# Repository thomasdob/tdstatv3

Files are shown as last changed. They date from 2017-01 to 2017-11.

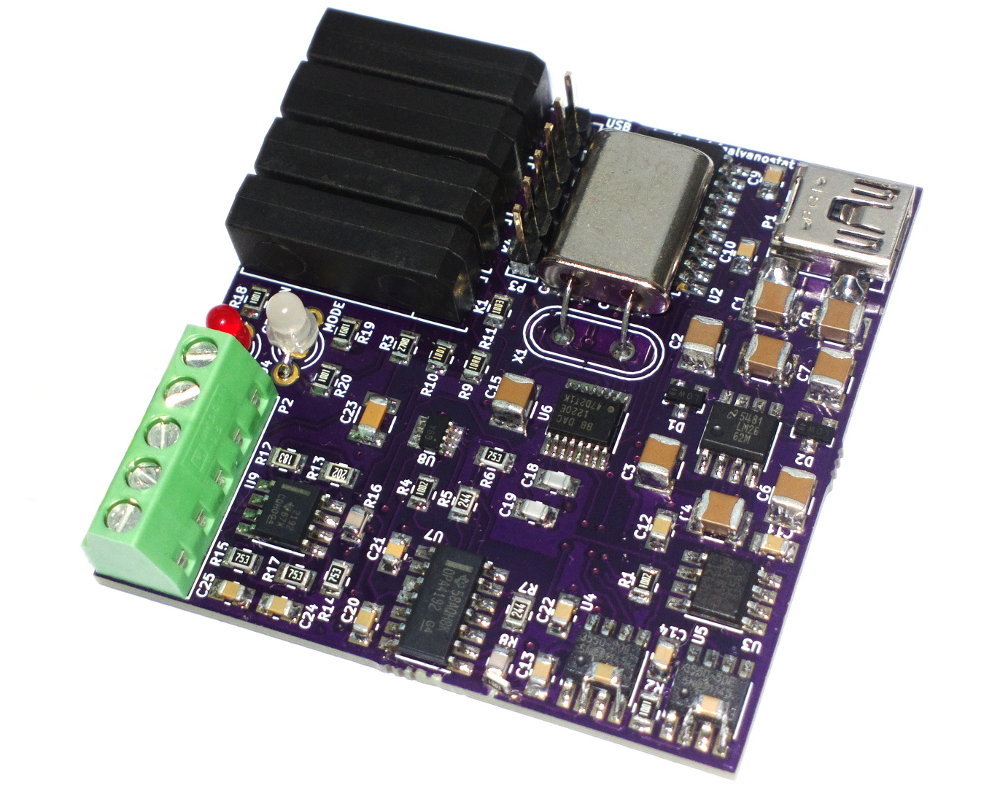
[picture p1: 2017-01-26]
photograph.jpg

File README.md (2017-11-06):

# TDstatv3
A USB-controlled potentiostat/galvanostat for thin-film battery characterization

## Introduction
This repository contains all the necessary design files to build your own USB-controlled potentiostat/galvanostat.
These files are intended as supplementary information accompanying the whitepaper at https://arxiv.org/pdf/1701.07650.pdf.

## Repository contents

### Directories
* `kicad`: KiCad design files (schematic diagram and PCB layout).
* `firmware`: Source code and compiled firmware for the PIC16F1459 microcontroller. Uses Microchip's XC8 compiler.
* `python`: Contains `tdstatv3.py`; run this file with Python 3 to bring up a GUI measurement tool.
* `gerber`: PCB design files in Gerber format, the universal standard for PCB manufacturing.
* `datasheets`: Datasheets in pdf format for the integrated circuits used in this design.
* `drivers`: Libusb drivers for Windows (not necessary on other operating systems).

### Files
* `full_schematic.pdf`: Complete schematic diagram in pdf format.
* `parts_list.txt`: Complete parts list, useful when ordering components.
* `pcb_3dview.png`: 3D renders of the PCB design, useful for verification of the PCB layout.
* `pcb_fabrication_diagram.pdf`: Front side of PCB with component locations and values, useful for circuit assembly.
* `photograph.jpg`: A photograph of the assembled circuit, using a PCB manufactured by [OSH Park](https://oshpark.com/).
* `LICENSE`: a copy of the GNU GPLv3 license.
* `README.md`: This file.

## USB access on Linux
In order to access the device without requiring root privileges, create a file
`/etc/udev/rules.d/99-tdstatv3.rules` containing the line

```
SUBSYSTEM=="usb", ATTRS{idVendor}=="a0a0", ATTRS{idProduct}=="0002", GROUP="plugdev", MODE="0666"
```
This assumes that the current user is a member of the `plugdev` group, and that the default USB Vendor and Product ID's
as coded in the microcontroller firmware are used; if not, these values need to be adjusted.

## Credits
* Thomas Dobbelaere
* email: thomas.dobbelaere@gmail.com

## License
The contents of this repository are licensed under the GNU General Public License (GPL).

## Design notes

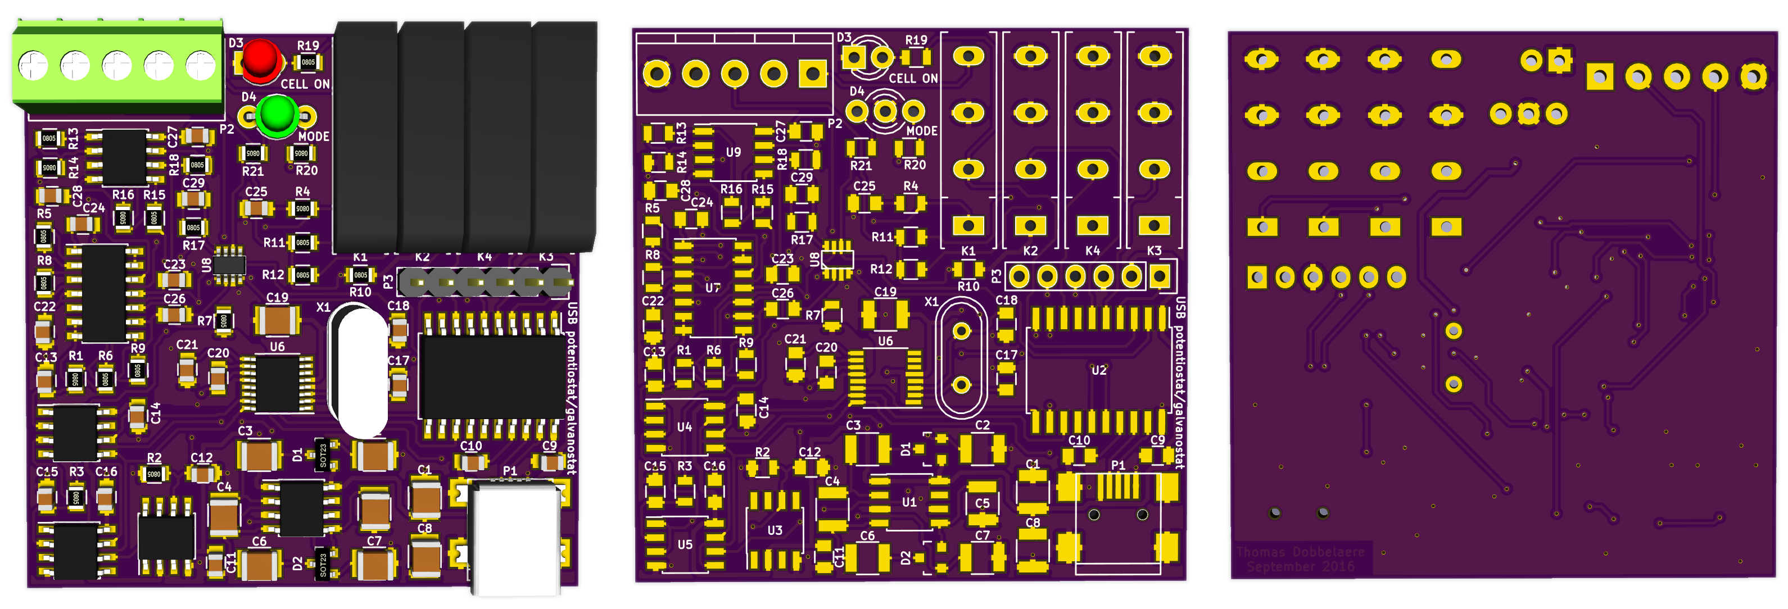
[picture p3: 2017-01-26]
pcb_3dview.png

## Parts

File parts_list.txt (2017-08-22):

Reference                     Description                                              Footprint     Digikey part #
R1,R3,R19-R21                 Resistor, 1k, 1%                                         0805          311-1.00KCRCT-ND
R2,R5                         Resistor, 10k, 1%                                        0805          311-10.0KCRCT-ND
R4                            Resistor, 27 ohm, 1%                                     0805          311-27.0CRCT-ND
R6,R8                         Precision resistor, 240k, 0.1% or better                 0805          RG20N240KWCT-ND
R7,R9,R15-R18                 Precision resistor, 75k, 0.1% or better                  0805          P75KBSCT-ND
R10                           Precision resistor, 10 ohm, 0.1% or better               0805          A119971CT-ND
R11                           Precision resistor, 1k, 0.1% or better                   0805          P1.0KDACT-ND
R12                           Precision resistor, 100k, 0.1% or better                 0805          P100KDACT-ND
R13                           Precision resistor, 18k, 0.1% or better                  0805          P18KDACT-ND
R14                           Precision resistor, 2k, 0.1% or better                   0805          P2.0KDACT-ND
C1-C8,C19                     Capacitor, 10 µF, ceramic                                1210          490-1867-1-ND
C9-C16, C22,C23,C25,C27,C28   Capacitor, 0.1 µF, ceramic                               0805          399-1168-1-ND
C17,C18,C26,C29               Capacitor, 12 pF, ceramic                                0805          1276-1120-1-ND
C20                           Capacitor, 3.3 nF, ceramic                               0805          399-10070-1-ND
C21                           Capacitor, 10 nF, ceramic                                0805          399-7992-1-ND
C24                           Capacitor, 4700 pF, ceramic                              0805          399-1155-1-ND
D1,D2                         Schottky diode, dual, BAT721S                            SOT-23        1727-3574-1-ND
D3                            LED, 3mm, red                                            -             754-1590-ND
D4                            LED, 3mm, dual red/green, common cathode                 -             754-1221-ND
U1                            Switched-capacitor voltage convertor, LM2662             SOIC-8        LM2662MX/NOPBCT-ND
U2                            8-bit USB microcontroller, PIC16F1459                    SOIC-20W      PIC16F1459-I/SO-ND
U3                            2.5V voltage reference, ADR421                           SOIC-8        ADR421ARZ-ND
U4,U5                         A/D convertor, MCP3550 (choose suffix by region)         SOIC-8        MCP3550-50(60)E/SN-ND
U6                            D/A convertor, DAC1220                                   SSOP-16       DAC1220E-ND
U7                            Op-amp, quad, OPA4192                                    SOIC-14       296-43159-1-ND
U8                            SPDT analog switch, DG449                                SOT-23-8      DG449DS-T1-E3CT-ND
U9                            Op-amp, dual, OPA2192                                    SOIC-8        296-42106-1-ND
X1                            Crystal oscillator, 2.5 MHz                              HC49          X1003-ND
K1-K4                         Reed relay, Coto 9007-05-01                              SIP           306-1063-ND
P1                            Mini USB receptacle, surface mount, type B               -             609-4700-1-ND
P2                            Terminal block, through hole, 5 position, 3.5mm spacing  -             277-5827-ND
P3                            Pin header, through hole, 6 pin                          -             S1011EC-06-ND

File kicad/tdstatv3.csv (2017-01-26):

Reference | Value | Footprint | Datasheet
U1 | LM2662 | Housings_SOIC:SOIC-8_3.9x4.9mm_Pitch1.27mm
C5 | 10 µF | Capacitors_SMD:C_1210
C6 | 10 µF | Capacitors_SMD:C_1210
C7 | 10 µF | Capacitors_SMD:C_1210
C4 | 10 µF | Capacitors_SMD:C_1210
D2 | BAT721S | TO_SOT_Packages_SMD:SOT-23
C3 | 10 µF | Capacitors_SMD:C_1210
D1 | BAT721S | TO_SOT_Packages_SMD:SOT-23
C2 | 10 µF | Capacitors_SMD:C_1210
U4 | MCP3550 | Housings_SOIC:SOIC-8_3.9x4.9mm_Pitch1.27mm
U6 | DAC1220 | Housings_SSOP:SSOP-16_3.9x4.9mm_Pitch0.635mm
U3 | ADR421 | Housings_SOIC:SOIC-8_3.9x4.9mm_Pitch1.27mm
U2 | PIC16F1459 | Housings_SOIC:SOIC-20W_7.5x12.8mm_Pitch1.27mm
P1 | Mini USB | Connect:USB_Mini-B
C11 | 0.1 µF | Capacitors_SMD:C_0805
C12 | 0.1 µF | Capacitors_SMD:C_0805
X1 | 2.5 MHz | Crystals:Crystal_HC49-U_Vertical
C17 | 12 pF | Capacitors_SMD:C_0805
C18 | 12 pF | Capacitors_SMD:C_0805
C21 | 10 nF | Capacitors_SMD:C_0805
C20 | 3.3 nF | Capacitors_SMD:C_0805
C19 | 10 µF | Capacitors_SMD:C_1210
U7 | OPA4192 | Housings_SOIC:SOIC-14_3.9x8.7mm_Pitch1.27mm
C25 | 0.1 µF | Capacitors_SMD:C_0805
R4 | 27R | Resistors_SMD:R_0805
C24 | 4700 pF | Capacitors_SMD:C_0805
R5 | 10k | Resistors_SMD:R_0805
K1 | 9007-05-01 | my_footprints:RELAY-9007
R6 | 240k* | Resistors_SMD:R_0805
R8 | 240k* | Resistors_SMD:R_0805
R7 | 75k* | Resistors_SMD:R_0805
R9 | 75k* | Resistors_SMD:R_0805
U5 | MCP3550 | Housings_SOIC:SOIC-8_3.9x4.9mm_Pitch1.27mm
C27 | 0.1 µF | Capacitors_SMD:C_0805
C28 | 0.1 µF | Capacitors_SMD:C_0805
C22 | 0.1 µF | Capacitors_SMD:C_0805
C23 | 0.1 µF | Capacitors_SMD:C_0805
C10 | 0.1 µF | Capacitors_SMD:C_0805
C9 | 0.1 µF | Capacitors_SMD:C_0805
P3 | ICSP | Pin_Headers:Pin_Header_Straight_1x06
D3 | CELL ON LED | LEDs:LED-3MM
D4 | MODE LED | my_footprints:DUO-LED-3mm
R19 | 1k | Resistors_SMD:R_0805
R20 | 1k | Resistors_SMD:R_0805
R21 | 1k | Resistors_SMD:R_0805
R10 | 10R* | Resistors_SMD:R_0805
R11 | 1k* | Resistors_SMD:R_0805
R12 | 100k* | Resistors_SMD:R_0805
U8 | DG449 | my_footprints:sot23-8
C14 | 0.1 µF | Capacitors_SMD:C_0805
C16 | 0.1 µF | Capacitors_SMD:C_0805
R2 | 10k | Resistors_SMD:R_0805
R3 | 1k | Resistors_SMD:R_0805
K2 | 9007-05-01 | my_footprints:RELAY-9007
K3 | 9007-05-01 | my_footprints:RELAY-9007
K4 | 9007-05-01 | my_footprints:RELAY-9007
R14 | 2k* | Resistors_SMD:R_0805
R13 | 18k* | Resistors_SMD:R_0805
R16 | 75k* | Resistors_SMD:R_0805
R15 | 75k* | Resistors_SMD:R_0805
R18 | 75k* | Resistors_SMD:R_0805
R17 | 75k* | Resistors_SMD:R_0805
U9 | OPA2192 | Housings_SOIC:SOIC-8_3.9x4.9mm_Pitch1.27mm
P2 | CELL | my_footprints:TerminalBlock_Phoenix_MKDS1_5_3mm5
C1 | 10 µF | Capacitors_SMD:C_1210
C8 | 10 µF | Capacitors_SMD:C_1210
R1 | 1k | Resistors_SMD:R_0805
C15 | 0.1 µF | Capacitors_SMD:C_0805
C13 | 0.1 µF | Capacitors_SMD:C_0805
C29 | 12 pF | Capacitors_SMD:C_0805
C26 | 12 pF | Capacitors_SMD:C_0805

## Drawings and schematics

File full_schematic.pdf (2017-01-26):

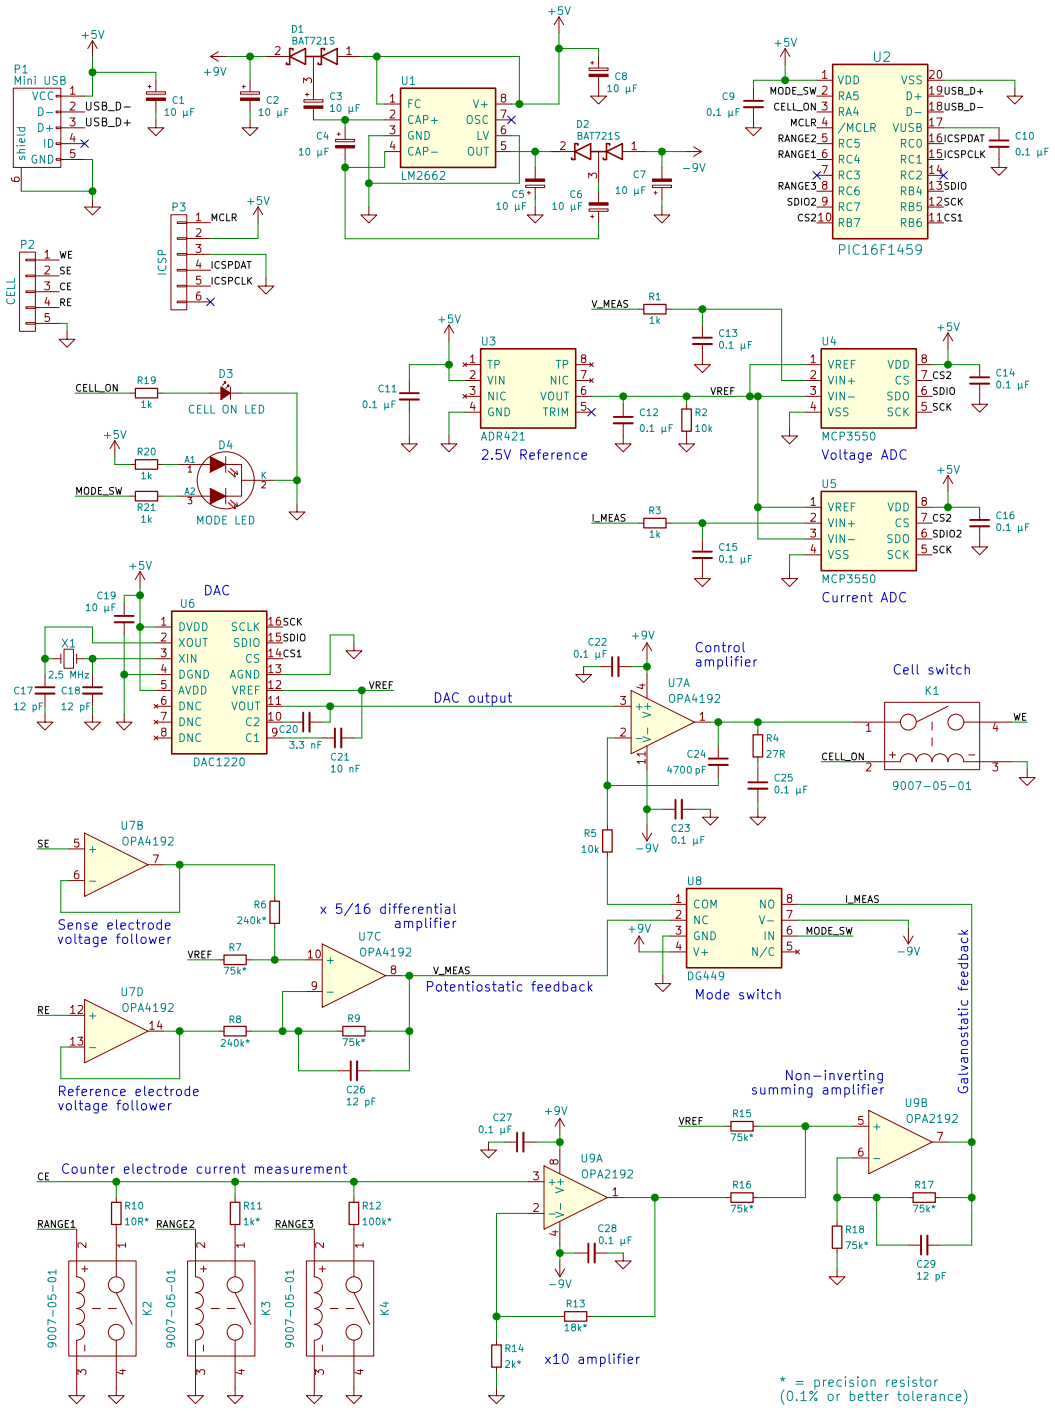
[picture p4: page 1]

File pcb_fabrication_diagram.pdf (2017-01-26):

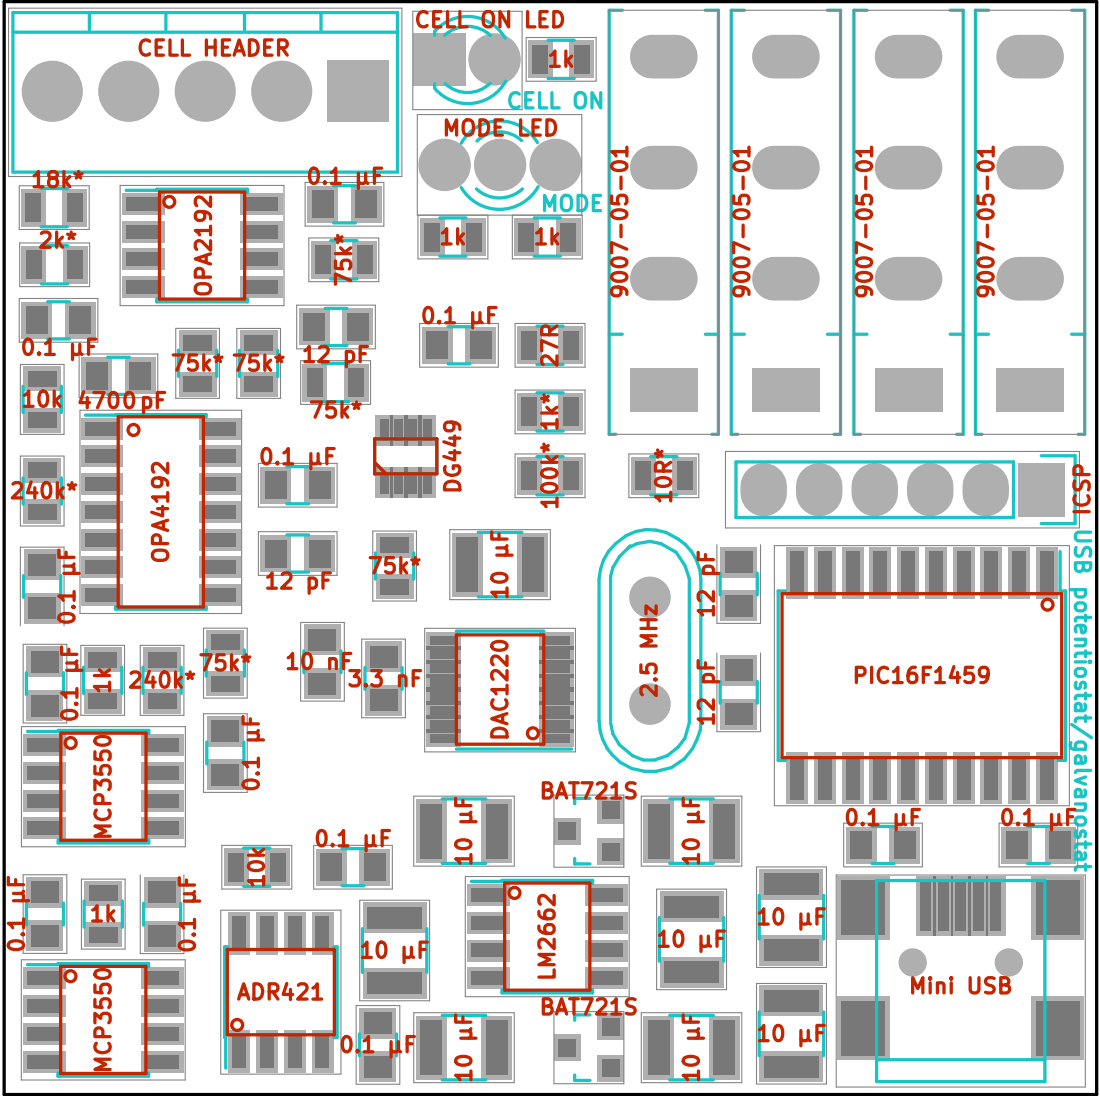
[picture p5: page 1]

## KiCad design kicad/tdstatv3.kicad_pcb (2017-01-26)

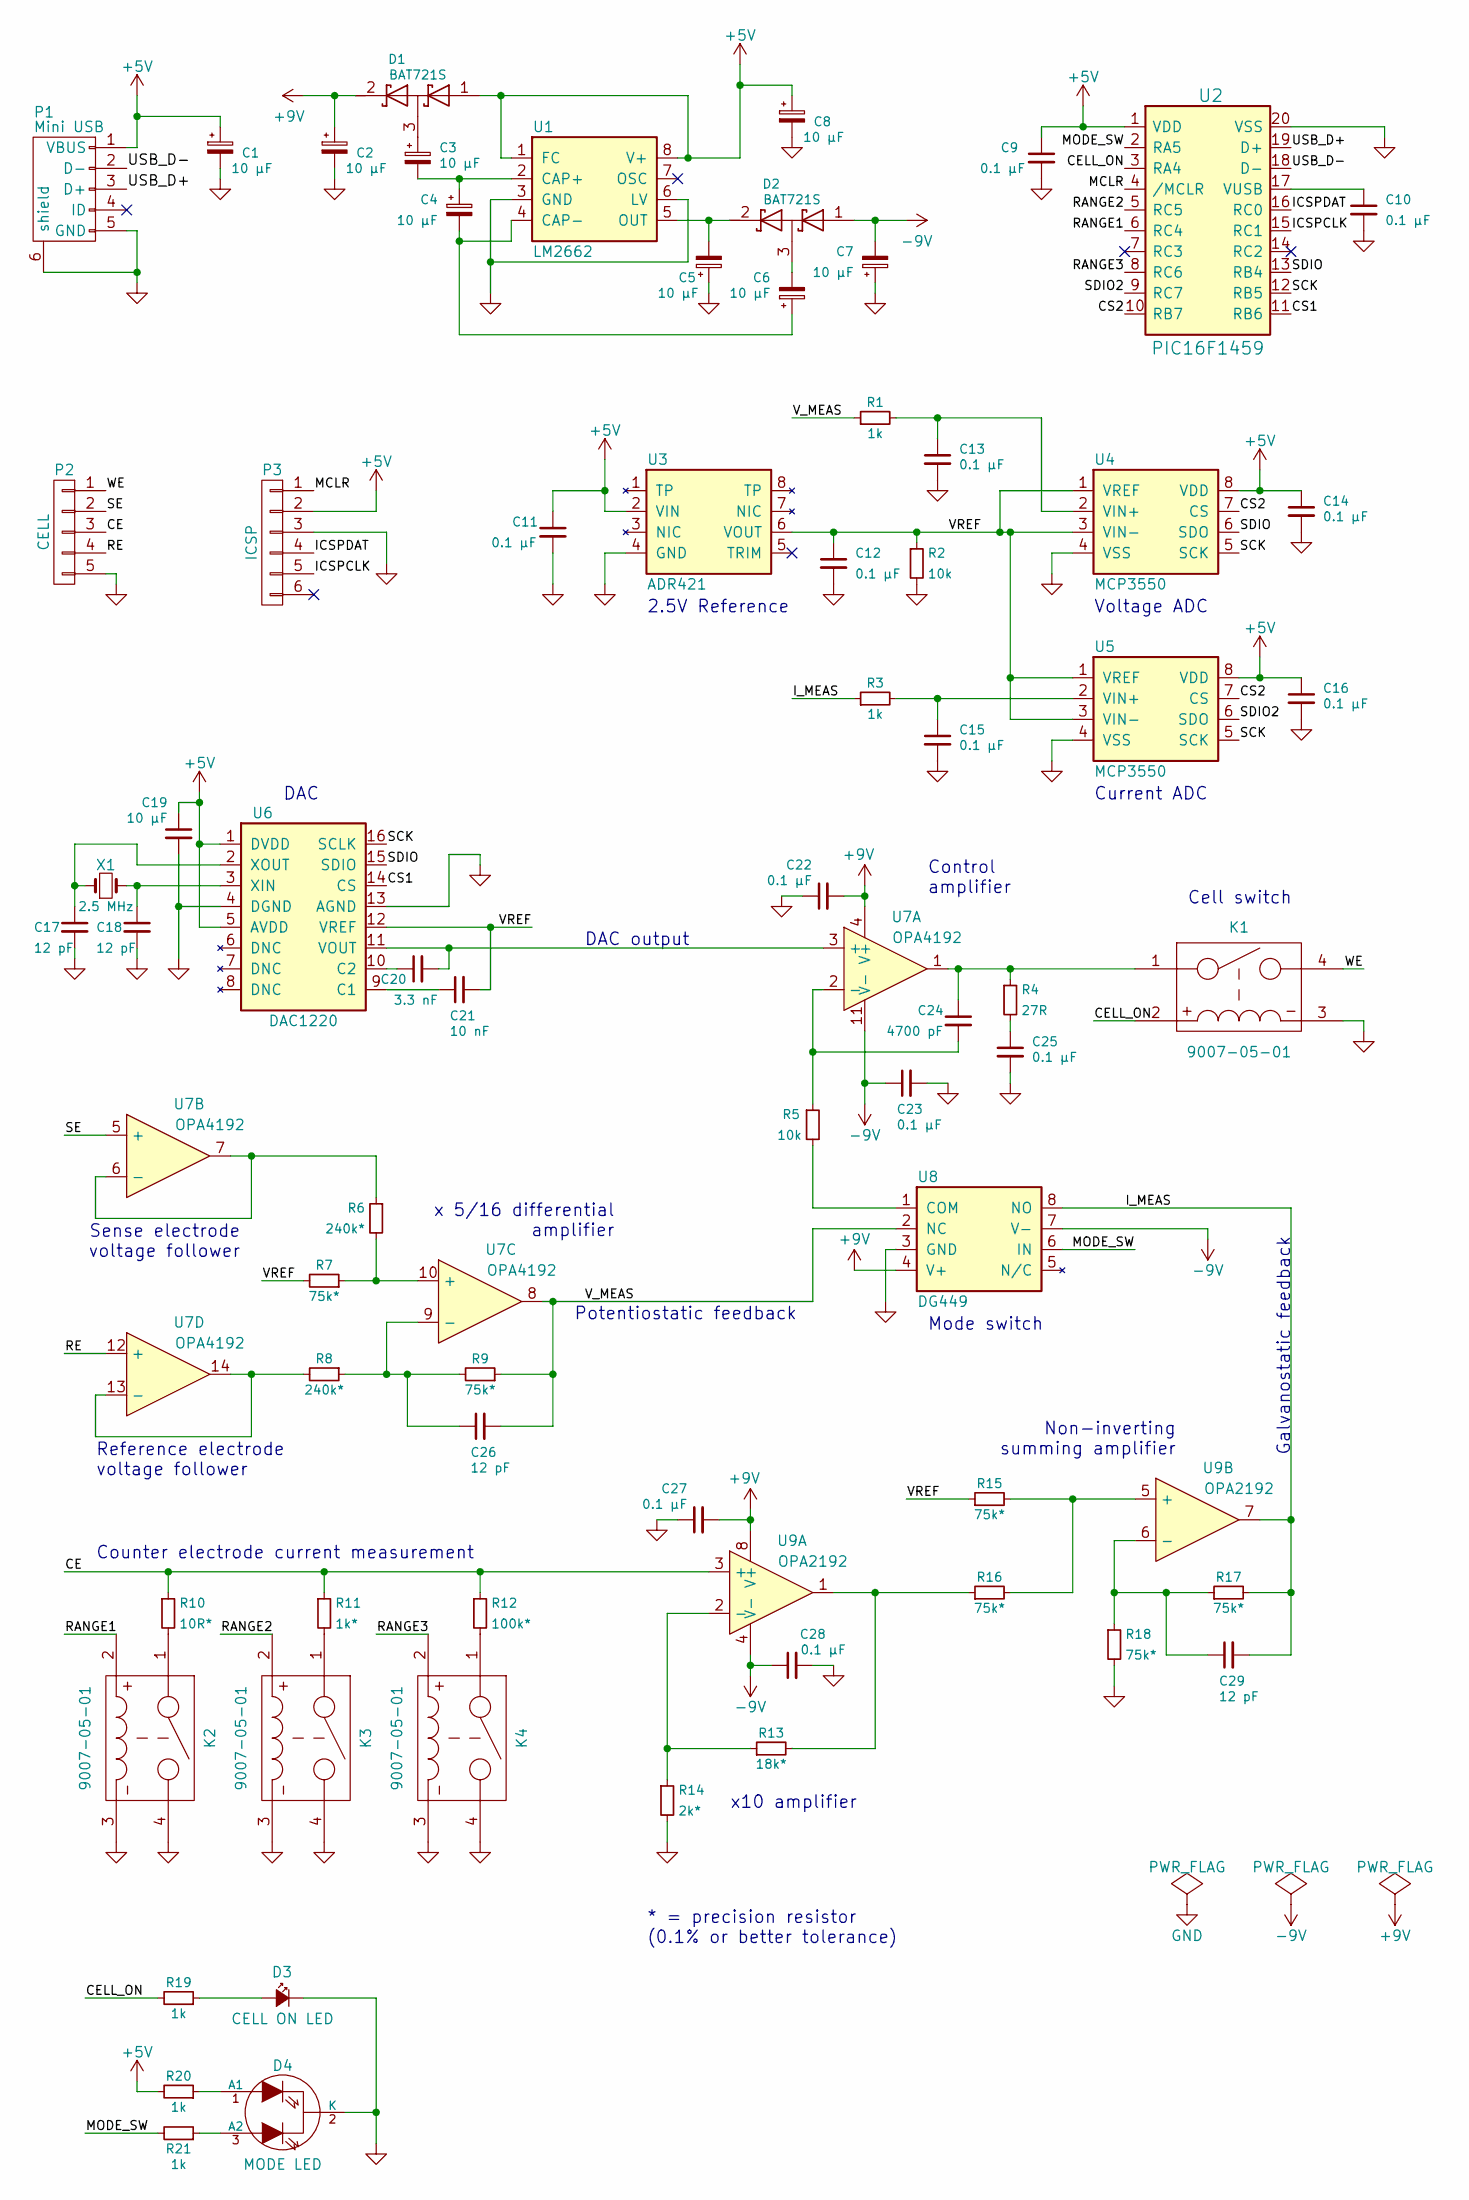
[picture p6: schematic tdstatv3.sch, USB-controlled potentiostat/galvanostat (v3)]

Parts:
C1, C2, C3, C4, C5, C6, C7, C8, C19: 10 µF; C_1210
C9, C10, C11, C12, C13, C14, C15, C16, C22, C23, C25, C27, C28: 0.1 µF; C_0805
C17, C18, C26, C29: 12 pF; C_0805
C20: 3.3 nF; C_0805
C21: 10 nF; C_0805
C24: 4700 pF; C_0805
D1, D2: BAT721S; SOT-23
D3: CELL ON LED; LED-3MM
D4: MODE LED; DUO-LED-3mm
K1, K2, K3, K4: 9007-05-01; RELAY-9007
P1: Mini USB; USB_Mini-B
P2: CELL; TerminalBlock_Phoenix_MKDS1_5_3mm5
P3: ICSP; Pin_Header_Straight_1x06
R1, R3, R19, R20, R21: 1k; R_0805
R2, R5: 10k; R_0805
R4: 27R; R_0805
R6, R8: 240k*; R_0805
R7, R9, R15, R16, R17, R18: 75k*; R_0805
R10: 10R*; R_0805
R11: 1k*; R_0805
R12: 100k*; R_0805
R13: 18k*; R_0805
R14: 2k*; R_0805
U1: LM2662; SOIC-8_3.9x4.9mm_Pitch1.27mm
U2: PIC16F1459; SOIC-20W_7.5x12.8mm_Pitch1.27mm
U3: ADR421; SOIC-8_3.9x4.9mm_Pitch1.27mm
U4, U5: MCP3550; SOIC-8_3.9x4.9mm_Pitch1.27mm
U6: DAC1220; SSOP-16_3.9x4.9mm_Pitch0.635mm
U7: OPA4192; SOIC-14_3.9x8.7mm_Pitch1.27mm
U8: DG449; sot23-8
U9: OPA2192; SOIC-8_3.9x4.9mm_Pitch1.27mm
X1: 2.5 MHz; Crystal_HC49-U_Vertical

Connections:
+5V: C1.1, C8.1, C9.1, C11.1, C14.1, C16.1, C19.1, D1.1 (A), P1.1 (VBUS), P3.2, R20.2, U1.1 (FC), U1.8 (V+), U2.1 (VDD), U3.2 (VIN), U4.8 (VDD), U5.8 (VDD), U6.1 (DVDD), U6.5 (AVDD)
+9V: C2.1, C22.2, C27.2, D1.2 (K), U7.4 (V+), U8.4 (V+), U9.8 (V+)
-9V: C7.2, C23.1, C28.1, D2.1 (A), U7.11 (V-), U8.7 (V-), U9.4 (V-)
/CE: P2.3, R10.1, R11.1, R12.1, U9.3 (+)
/CELL_ON: K1.2 (+), R19.2, U2.3 (RA4)
/CS1: U2.11 (RB6), U6.14 (CS)
/CS2: U2.10 (RB7), U4.7 (CS), U5.7 (CS)
/ICSPCLK: P3.5, U2.15 (RC1)
/ICSPDAT: P3.4, U2.16 (RC0)
/I_MEAS: C29.2, R3.1, R17.2, U8.8 (NO), U9.7
/MCLR: P3.1, U2.4 (/MCLR)
/MODE_SW: R21.2, U2.2 (RA5), U8.6 (IN)
/RANGE1: K2.2 (+), U2.6 (RC4)
/RANGE2: K3.2 (+), U2.5 (RC5)
/RANGE3: K4.2 (+), U2.8 (RC6)
/RE: P2.4, U7.12 (+)
/SCK: U2.12 (RB5), U4.5 (SCK), U5.5 (SCK), U6.16 (SCLK)
/SDIO: U2.13 (RB4), U4.6 (SDO), U6.15 (SDIO)
/SDIO2: U2.9 (RC7), U5.6 (SDO)
/SE: P2.2, U7.5 (+)
/USB_D+: P1.3 (D+), U2.19 (D+)
/USB_D-: P1.2 (D-), U2.18 (D-)
/VREF: C12.1, C21.2, R2.1, R7.2, R15.1, U3.6 (VOUT), U4.1 (VREF), U4.3 (VIN-), U5.1 (VREF), U5.3 (VIN-), U6.12 (VREF)
/V_MEAS: C26.2, R1.1, R9.1, U7.8, U8.2 (NC)
/WE: K1.4, P2.1
GND: C1.2, C2.2, C5.1, C7.1, C8.2, C9.2, C10.2, C11.2, C12.2, C13.2, C14.2, C15.2, C16.2, C17.2, C18.2, C19.2, C22.1, C23.2, C25.2, C27.1, C28.2, D3.1 (K), D4.2 (K), K1.3, K2.3, K2.4, K3.3, K3.4, K4.3, K4.4, P1.5 (GND), P1.6 (shield), P2.5, P3.3, R2.2, R14.2, R18.2, U1.3 (GND), U1.6 (LV), U2.20 (VSS), U3.4 (GND), U4.4 (VSS), U5.4 (VSS), U6.4 (DGND), U6.13 (AGND), U8.3 (GND)
unnamed: C3.1, D1.3 (common)
unnamed: C3.2, C4.1, U1.2 (CAP+)
unnamed: C4.2, C6.1, U1.4 (CAP-)
unnamed: C5.2, D2.2 (K), U1.5 (OUT)
unnamed: C6.2, D2.3 (common)
unnamed: C10.1, U2.17 (VUSB)
unnamed: C13.1, R1.2, U4.2 (VIN+)
unnamed: C15.1, R3.2, U5.2 (VIN+)
unnamed: C17.1, U6.2 (XOUT), X1.1
unnamed: C18.1, U6.3 (XIN), X1.2
unnamed: C20.1, U6.10 (C2)
unnamed: C20.2, U6.11 (VOUT), U7.3 (+)
unnamed: C21.1, U6.9 (C1)
unnamed: C24.1, K1.1, R4.1, U7.1
unnamed: C24.2, R5.1, U7.2 (-)
unnamed: C25.1, R4.2
unnamed: C26.1, R8.1, R9.2, U7.9 (-)
unnamed: C29.1, R17.1, R18.1, U9.6 (-)
unnamed: D3.2 (A), R19.1
unnamed: D4.1 (A1), R20.1
unnamed: D4.3 (A2), R21.1
unnamed: K2.1, R10.2
unnamed: K3.1, R11.2
unnamed: K4.1, R12.2
unnamed: R5.2, U8.1 (COM)
unnamed: R6.1, U7.6 (-), U7.7
unnamed: R6.2, R7.1, U7.10 (+)
unnamed: R8.2, U7.13 (-), U7.14
unnamed: R13.1, R14.1, U9.2 (-)
unnamed: R13.2, R16.1, U9.1
unnamed: R15.2, R16.2, U9.5 (+)

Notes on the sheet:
x 5/16 differential amplifier
Sense electrode voltage follower
Reference electrode voltage follower
Counter electrode current measurement
x10 amplifier
Non-inverting summing amplifier
Potentiostatic feedback
Galvanostatic feedback
Current ADC
Voltage ADC
2.5V Reference
Control amplifier
DAC
Mode switch
Cell switch
DAC output
* = precision resistor (0.1% or better tolerance)

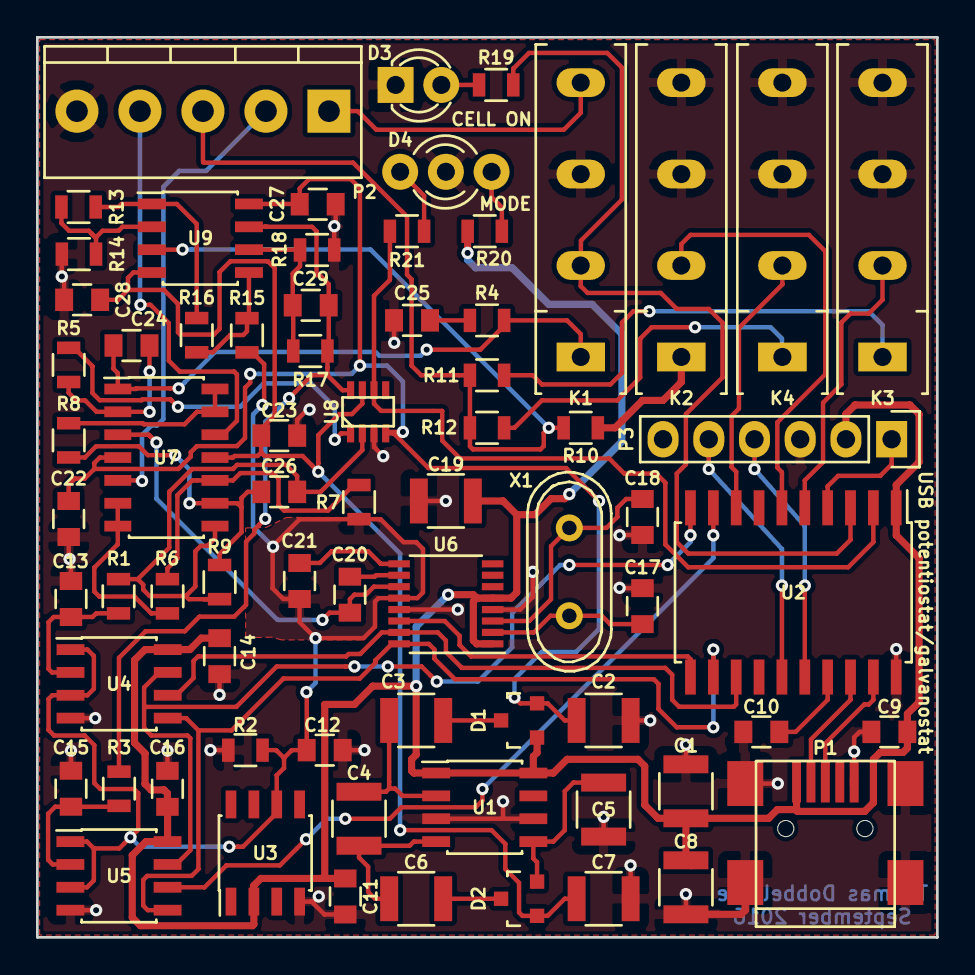
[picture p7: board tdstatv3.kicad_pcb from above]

Board: 2 copper layers, 50.0 x 50.0 mm, 71 parts (0 on the bottom side), 57 nets.

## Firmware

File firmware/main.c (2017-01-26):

/*
 * USB Potentiostat/galvanostat firmware
 *
 * This code makes use of Signal 11's M-Stack USB stack to implement 
 * communication through raw USB bulk transfers. Commands are received
 * as ASCII strings on EP1 OUT. They are then interpreted and executed;
 * they either change the state of output pins, or cause data to be read
 * from / written to the MCP3550 (ADC) or DAC1220 (DAC) using a software
 * SPI implementation. The resulting data, or an "OK" message, is sent as
 * a reply on EP1 IN. The USB service is interrupt-driven.
 *
 * Thomas Dobbelaere
 * CoCooN research group
 * 2016-06-07
 */

#include "usb.h"
#include <xc.h>
#include <string.h>
#include "usb_config.h"
#include "usb_ch9.h"
#include "spi_software.h"
#include "Flash.h"
#include "HEFlash.h"

// PIC16F1459 configuration bit settings:
// CONFIG1
#pragma config FOSC = INTOSC    // Oscillator Selection Bits (INTOSC oscillator: I/O function on CLKIN pin)
#pragma config WDTE = OFF       // Watchdog Timer Enable (WDT disabled)
#pragma config PWRTE = OFF      // Power-up Timer Enable (PWRT disabled)
#pragma config MCLRE = OFF      // MCLR Pin Function Select (MCLR/VPP pin function is digital input)
#pragma config CP = OFF         // Flash Program Memory Code Protection (Program memory code protection is disabled)
#pragma config BOREN = ON       // Brown-out Reset Enable (Brown-out Reset enabled)
#pragma config CLKOUTEN = OFF   // Clock Out Enable (CLKOUT function is disabled. I/O or oscillator function on the CLKOUT pin)
#pragma config IESO = OFF       // Internal/External Switchover Mode (Internal/External Switchover Mode is disabled)
#pragma config FCMEN = OFF      // Fail-Safe Clock Monitor Enable (Fail-Safe Clock Monitor is disabled)

// CONFIG2
#pragma config WRT = OFF        // Flash Memory Self-Write Protection (Write protection off)
#pragma config CPUDIV = NOCLKDIV// CPU System Clock Selection Bit (NO CPU system divide)
#pragma config USBLSCLK = 48MHz // USB Low Speed Clock Selection bit (System clock expects 48 MHz, FS/LS USB CLKENs divide-by is set to 8.)
#pragma config PLLMULT = 3x     // PLL Multipler Selection Bit (3x Output Frequency Selected)
#pragma config PLLEN = ENABLED  // PLL Enable Bit (3x or 4x PLL Enabled)
#pragma config STVREN = ON      // Stack Overflow/Underflow Reset Enable (Stack Overflow or Underflow will cause a Reset)
#pragma config BORV = LO        // Brown-out Reset Voltage Selection (Brown-out Reset Voltage (Vbor), low trip point selected.)
#pragma config LPBOR = OFF      // Low-Power Brown Out Reset (Low-Power BOR is disabled)
#pragma config LVP = OFF        // Low-Voltage Programming Enable (High-voltage on MCLR/VPP must be used for programming)

#define _XTAL_FREQ 48000000     // 48 MHz CPU clock frequency

#define MODE_SW_PIN LATAbits.LATA5
#define MODE_SW_TRIS TRISAbits.TRISA5
#define CELL_ON_PIN LATAbits.LATA4
#define CELL_ON_TRIS TRISAbits.TRISA4
#define CELL_ON  1
#define CELL_OFF 0
#define POTENTIOSTATIC  0
#define GALVANOSTATIC  1
#define INPUT  1
#define OUTPUT 0
#define RANGE1_PIN LATCbits.LATC4
#define RANGE1_TRIS TRISCbits.TRISC4
#define RANGE2_PIN LATCbits.LATC5
#define RANGE2_TRIS TRISCbits.TRISC5
#define RANGE3_PIN LATCbits.LATC6
#define RANGE3_TRIS TRISCbits.TRISC6

static const uint8_t* received_data;
static uint8_t received_data_length;
static uint8_t* transmit_data;
static uint8_t transmit_data_length;
static uint8_t heflashbuffer[FLASH_ROWSIZE];

void InitializeIO()
{
	OSCCONbits.IRCF = 0b1111; // 0b1111 = 16MHz HFINTOSC postscaler
	ANSELA = 0x00; // digital I/O on PORTA
	ANSELB = 0x00; // digital I/O on PORTB
	ANSELC = 0x00; // digital I/O on PORTC
	APFCON = 0x00; // no funny alternate pins
	MODE_SW_TRIS = OUTPUT;
	MODE_SW_PIN = POTENTIOSTATIC; // initialize mode to potentiostatic
	CELL_ON_TRIS = OUTPUT;
	CELL_ON_PIN = CELL_OFF; // initialize cell to off position
	RANGE1_TRIS = OUTPUT;
	RANGE2_TRIS = OUTPUT;
	RANGE3_TRIS = OUTPUT;
	RANGE1_PIN = 1; // initialize range to range 1
	RANGE2_PIN = 0;
	RANGE3_PIN = 0;
	InitializeSPI();
	__delay_ms(25); // power-up delay - necessary for DAC1220
	DAC1220_Reset();
	__delay_ms(25);
	DAC1220_Init();
	HEFLASH_readBlock(heflashbuffer, 2, FLASH_ROWSIZE); // get dac calibration
	DAC1220_Write3Bytes(8, heflashbuffer[0], heflashbuffer[1], heflashbuffer[2]); // apply dac calibration
	DAC1220_Write3Bytes(12, heflashbuffer[3], heflashbuffer[4], heflashbuffer[5]); 
}

void command_unknown()
{
	const uint8_t* reply = "?";
    strcpy(transmit_data, reply);
    transmit_data_length = strlen(reply);
}

void send_OK()
{
	const uint8_t* reply = "OK";
    strcpy(transmit_data, reply);
    transmit_data_length = strlen(reply);
}

void command_cell_on()
{
	CELL_ON_PIN = CELL_ON;
	send_OK();
}

void command_cell_off()
{
	CELL_ON_PIN = CELL_OFF;
	send_OK();
}

void command_mode_potentiostatic()
{
	MODE_SW_PIN = POTENTIOSTATIC;
	send_OK();
}

void command_mode_galvanostatic()
{
	MODE_SW_PIN = GALVANOSTATIC;
	send_OK();
}

void command_range1()
{
    RANGE1_PIN = 1;
    __delay_ms(10); // make the new relay setting before breaking the old one
    RANGE2_PIN = 0;
    RANGE3_PIN = 0;
	send_OK();
}

void command_range2()
{
    RANGE2_PIN = 1;
    __delay_ms(10); // make the new relay setting before breaking the old one
    RANGE1_PIN = 0;
    RANGE3_PIN = 0;
	send_OK();
}

void command_range3()
{
    RANGE3_PIN = 1;
    __delay_ms(10); // make the new relay setting before breaking the old one
    RANGE1_PIN = 0;
    RANGE2_PIN = 0;
	send_OK();
}

void command_set_dac(const uint8_t* dac_data)
{
	DAC1220_Write3Bytes(0, dac_data[0], dac_data[1], dac_data[2]);
	send_OK();
}

void command_calibrate_dac()
{
	DAC1220_SelfCal();
	__delay_ms(500); // wait until calibration is finished
	uint8_t data[6];
	DAC1220_Read3Bytes(8, data, data+1, data+2); // get calibration data
	DAC1220_Read3Bytes(12, data+3, data+4, data+5);
	HEFLASH_writeBlock(2, data, 6); // save calibration data to HEFLASH
	send_OK();
}

void command_read_adc()
{
	uint8_t adc_data[6];
	if(MCP3550_Read(adc_data))
	{
		transmit_data_length=6;
		memcpy(transmit_data, adc_data, transmit_data_length);
	}
	else
	{
		const uint8_t* reply = "WAIT";
		strcpy(transmit_data, reply);
		transmit_data_length = strlen(reply);
	}
}

void command_read_offset()
{
	HEFLASH_readBlock(heflashbuffer, 1, FLASH_ROWSIZE);
	transmit_data_length=6;
	memcpy(transmit_data, heflashbuffer, transmit_data_length);
}

void command_save_offset(const uint8_t* offset_data)
{
	HEFLASH_writeBlock(1, offset_data, 6);
	send_OK();
}

void command_read_shuntcalibration()
{
	HEFLASH_readBlock(heflashbuffer, 3, FLASH_ROWSIZE);
	transmit_data_length=6;
	memcpy(transmit_data, heflashbuffer, transmit_data_length);
}

void command_save_shuntcalibration(const uint8_t* shuntcalibration_data)
{
	HEFLASH_writeBlock(3, shuntcalibration_data, 6);
	send_OK();
}

void command_read_dac_cal()
{
	HEFLASH_readBlock(heflashbuffer, 2, FLASH_ROWSIZE);
	transmit_data_length=6;
	memcpy(transmit_data, heflashbuffer, transmit_data_length);
}

void command_set_dac_cal(const uint8_t* dac_cal_data)
{
	HEFLASH_writeBlock(2, dac_cal_data, 6);
	DAC1220_Write3Bytes(8, dac_cal_data[0], dac_cal_data[1], dac_cal_data[2]);
	DAC1220_Write3Bytes(12, dac_cal_data[3], dac_cal_data[4], dac_cal_data[5]);
	send_OK();
}

void interpret_command() {
    if (received_data_length == 7 && strncmp(received_data,"CELL ON",7) == 0)
        command_cell_on();
    else if (received_data_length == 8 && strncmp(received_data,"CELL OFF",8) == 0)
        command_cell_off();
    else if (received_data_length == 14 && strncmp(received_data,"POTENTIOSTATIC",14) == 0)
        command_mode_potentiostatic();
    else if (received_data_length == 13 && strncmp(received_data,"GALVANOSTATIC",13) == 0)
        command_mode_galvanostatic();
    else if (received_data_length == 7 && strncmp(received_data,"RANGE 1",7) == 0)
        command_range1();
    else if (received_data_length == 7 && strncmp(received_data,"RANGE 2",7) == 0)
        command_range2();
    else if (received_data_length == 7 && strncmp(received_data,"RANGE 3",7) == 0)
        command_range3();
    else if (received_data_length == 10 && strncmp(received_data,"DACSET ",7) == 0)
	command_set_dac(received_data+7);
    else if (received_data_length == 6 && strncmp(received_data,"DACCAL",6) == 0)
	command_calibrate_dac();
    else if (received_data_length == 7 && strncmp(received_data,"ADCREAD",7) == 0)
	command_read_adc();
    else if (received_data_length == 10 && strncmp(received_data,"OFFSETREAD",10) == 0)
	command_read_offset();
    else if (received_data_length == 17 && strncmp(received_data,"OFFSETSAVE ",11) == 0)
	command_save_offset(received_data+11);
    else if (received_data_length == 9 && strncmp(received_data,"DACCALGET",9) == 0)
	command_read_dac_cal();
    else if (received_data_length == 16 && strncmp(received_data,"DACCALSET ",10) == 0)
	command_set_dac_cal(received_data+10);
    else if (received_data_length == 12 && strncmp(received_data,"SHUNTCALREAD",12) == 0)
	command_read_shuntcalibration();
    else if (received_data_length == 19 && strncmp(received_data,"SHUNTCALSAVE ",13) == 0)
	command_save_shuntcalibration(received_data+13);
    else
        command_unknown();
}

int main(void)
{
	InitializeIO();

	// Enable Active clock-tuning from the USB
	ACTCONbits.ACTSRC = 1; // 1=USB
	ACTCONbits.ACTEN = 1;

	// Configure interrupts
	INTCONbits.PEIE = 1;
	INTCONbits.GIE = 1;

	// Initialize USB
	usb_init();

	while (1)
	{
		if (usb_is_configured() && usb_out_endpoint_has_data(1)) // wait for data received from host
		{
			if (!usb_in_endpoint_halted(1))
			{
				while (usb_in_endpoint_busy(1)) // wait for EP1 IN to become free
					;
				received_data_length = usb_get_out_buffer(1, &received_data); // get memory location and length of received data
				transmit_data = usb_get_in_buffer(1); // get memory location of data to transmit
				interpret_command(); // this reads received_data and sets transmit_data and transmit_data_length
				usb_send_in_buffer(1, transmit_data_length); // send the data back
			}
			usb_arm_out_endpoint(1);
		}
	}

	return 0;
}

void interrupt isr()
{
	usb_service();
}
